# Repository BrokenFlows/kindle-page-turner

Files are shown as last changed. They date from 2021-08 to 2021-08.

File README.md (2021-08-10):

# Kindle Page Turner

Photo of Kindle Page Turner on a desk

The code in this repository, along with the physical components outlined in the [bill of materials](#Bill-of-Materials), can be used to turn pages of a Kindle e-reader with external buttons.

I made this project to allow me to more comfortably read books, something I struggle with as a result of chronic pain. I use my hands, in a relaxed position, to press the buttons. However, one could use longer wires and potentially press the buttons with their feet to avoid using arms at all.

Animatetd GIF of Kindle Page Turner on a desk

This project allows the user to turn pages on a Kindle using external buttons, when the kindle is in a stand.
Navigating the user interface of the Kindle is outside the capabilities of this project.

## Instructions
These instructions will serve as a rough guide of the steps required to make this project.
The project, as it stands, requires off-the-shelf electronic components, custom 3D printed pieces, and relatively simple soldering.

### Hardware
The [tools](#Tools) and [materials](#Bill-of-Materials) will be used to assemble the final product, shown above. If you have acquired the items required, you can follow the steps outlined in the [assembly](#Pre-Assembly) section.

#### Tools
- Soldering Iron
- Solder Wire
- 3D Printer/ 3D Printing Service/ or some means of mimicking [the case and parts](./stls/) listed below
- Scissors/ wire cutter
- **Optional:** wire stripper

#### Bill of Materials
Item # | Quantity | Part # | Part Name                                                                         | Description
------:|---------:|-------:|:----------------------------------------------------------------------------------|-------------
1      | 1        | G0910  | [Kindle](https://www.amazon.co.uk/dp/B07FQ4XCR1)                                  | The 10th Generation Kindle e-reader
2      | 1        | N/A    | [kindle_holder_and_servo_housing.stl](./stls/kindle_holder_and_servo_housing.stl) | A case for the Kindle
3      | 1        | N/A    | [pico_housing.stl](./stls/pico_housing.stl)                                       | The housing for the Raspberry Pi Pico at the back of the case
4      | 1        | N/A    | [pico_cover.stl](./stls/pico_cover.stl)                                           | A cover for the Raspberry Pi Pico Housing, to keep wires contained
5      | 1        | N/A    | [servo_horn_sheaths.stl](./stls/servo_horn_sheaths.stl)                           | For attaching stylus tips pads to the servo motors
6      | 2        | N/A    | [Stylus Pen Tips](https://www.ebay.ie/itm/174215638532)                           | Capacitive stylus tips for the touch screen
7      | 2        | SG90   | [SG90 Servo Motor](https://www.ebay.ie/itm/373323581713)                          | Servo motors for moving the stylus tips
8      | 1        | SCO915 | [Raspberry Pi Pico](https://www.raspberrypi.org/products/raspberry-pi-pico/)      | Raspberry Pi Pico Microcontroller
9      | 1        | N/A    | Micro-USB cable                                                                   | A power cable for the Raspberry Pi Pico
10     | 1        | N/A    | [Tablet holder](https://www.amazon.co.uk/gp/product/B074GNPSC7/)                  | **Optional:** Tablet holder for positioning the kindle at a comfortable height hands-free
11     | 6        | N/A    | [Wires](https://www.ebay.ie/itm/232901601951)                                     | Lengths of wire, to your preference (I used over 4 m of wire)
12     | 2        | N/A    | [Buttons](https://www.ebay.ie/itm/224192810260) or [Key Switches](https://splitkb.com/collections/switches-and-keycaps) | Buttons or Switches to push when wanting to turn the page on the Kindle — I use light-weight low-profile choc switches

#### 3D Printing
I recommend 3D printing the stl files at the following settings:
Setting         | Value
:---------------|-----:
Filament        | PLA
Nozzle Diameter | < 0.4 mm
Layer Height    | < 0.2 mm
Infill          | 20% <
Supports        | Off

#### Pre-Assembly
1. Place the servo motors into their respective housings, on the left and right sides of the Kindle housing, with their wires through the holes at the back. If the servos have connectors at the end of the wires, cut the connectors off before separating the wires by ~7 cm and stripping the ends.
2. Solder the button pins, that are connected when the button is pressed, to lengths of wire that are long enough to reach a desk or lap from where the Kindle will be used. I used 1m of wire to each button pin I was connecting.
3. To avoid the wires tangling, it is recommended that you twist, or secure at regular intervals, the wires used for the buttons.

We'll complete the assembly after dealing with the circuitry portion.

#### Circuit
In this section, we'll solder the circuit to match the following diagram:
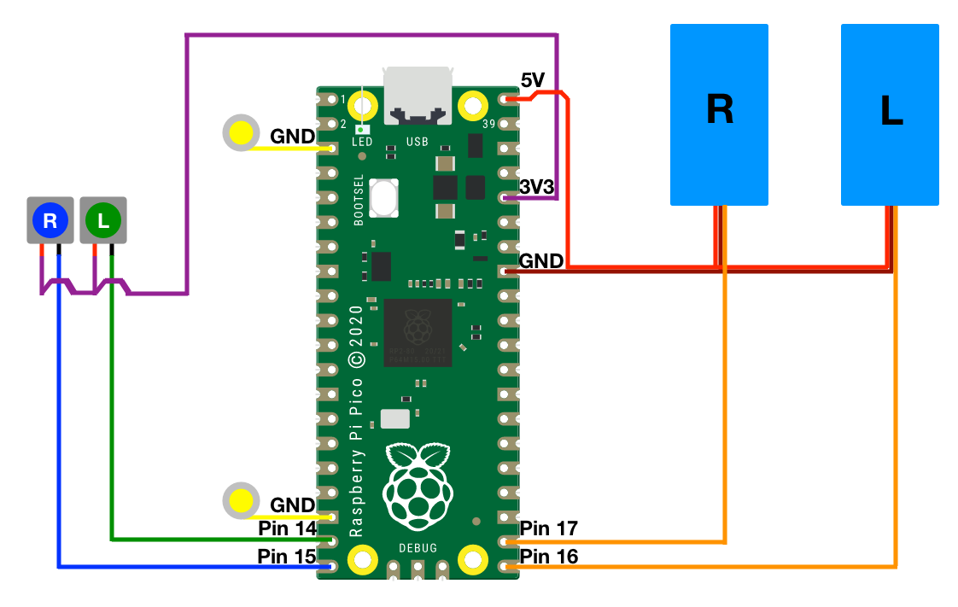
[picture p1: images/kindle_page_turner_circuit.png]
Circuit Diagram


- The buttons register a click when 3.3 V reaches their respective pins. The buttons are illustrated on the left side of the diagram.
- The stylus tips must be grounded for the Kindle to detect their taps. These are shown as the yellow lines and circles to the left of the Pico.
- The servos require 5 V to their red wires, their brown wires to be grounded, and their orange wires connected to the pins labelled on the right of the controller.

Use the [soldering tools](#Tools) to create mechanical and electrical connections between the components, as shown in the diagram.

#### Assembly
With the circuit ready, complete the following steps:
1. Feed the grounded wires through the servo horn sheaths. Make a connection here to the stylus tip, so that the tips will be grounded by the wires.
2. Secure the horns to the servos so that the end of their range will allow the stylus tip to reach the screen.
3. Put the servo horn sheaths, with wires and stylus tips attached, onto the servo horn.
4. Tidy the circuit into the Pico housing.
5. Slip the Pico Housing into the back of the Kindle case.
6. Cover the Pico and wiring with the housing cover.

At this point we will load the software onto the Pico.

### Software
I recommend following [this article](https://www.twilio.com/blog/programming-raspberry-pi-pico-microcontroller-micropython) on how to install micropython and transfer files onto the Raspberry Pi Pico.
If you copy [main.py](./main.py) onto the Raspberry Pi Pico, after installing micropython and setting up the hardware, it should allow buttons to turn the pages of the kindle.

### Testing
Once the software is loaded, each time the Pico is restarted it should flash a green LED for 1s. This will signal that the software was loaded successfully.
Then, you should try pressing the buttons to see if the servos move as expected.
If they do not, review the previous steps to resolve your issue.

It is recommended not to have your Kindle in the case when first testing, should the servos try to rotate past the screen.
If the rotation is off, reattach the servo horns to a better angle and try again.

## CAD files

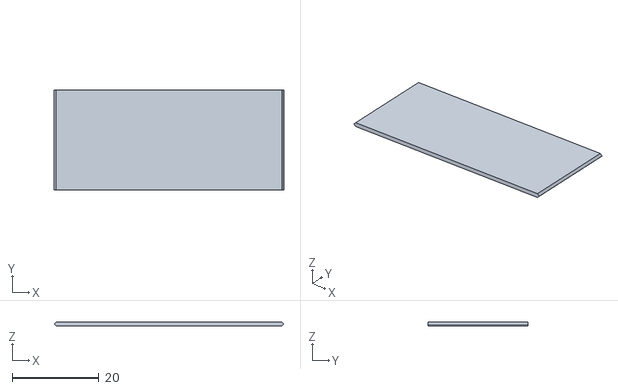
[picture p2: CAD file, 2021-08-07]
stls/pico_cover.stl
53.0 x 23.0 x 0.997

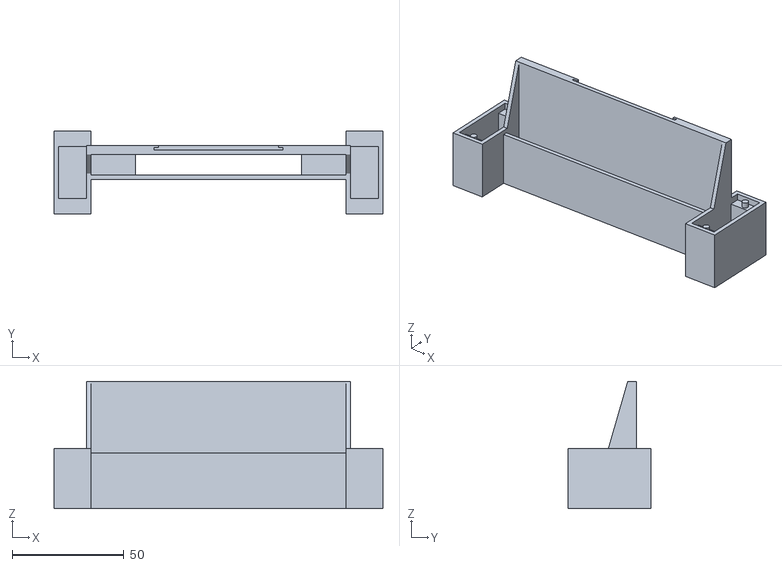
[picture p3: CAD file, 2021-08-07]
stls/kindle_holder_and_servo_housing.stl
147.5 x 37.0 x 57.0

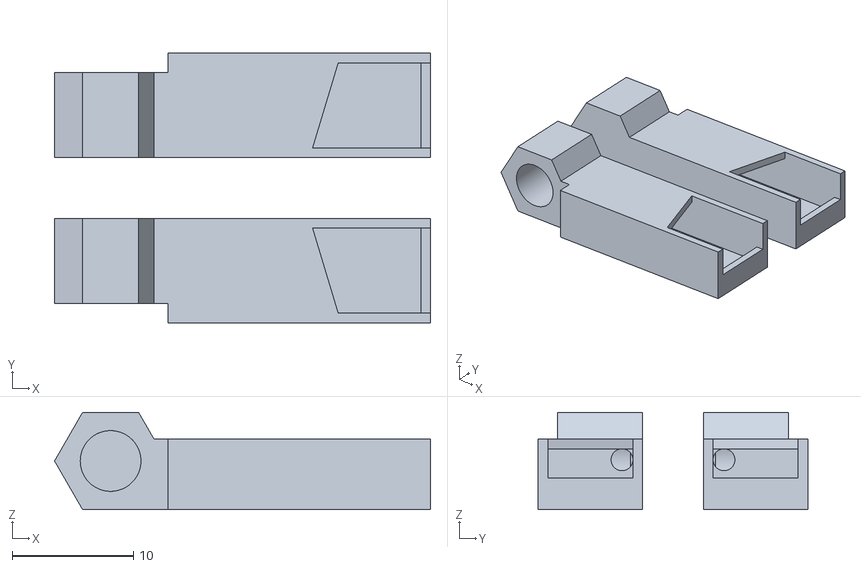
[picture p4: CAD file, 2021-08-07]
stls/servo_horn_sheaths.stl
31.0 x 22.2 x 8.00

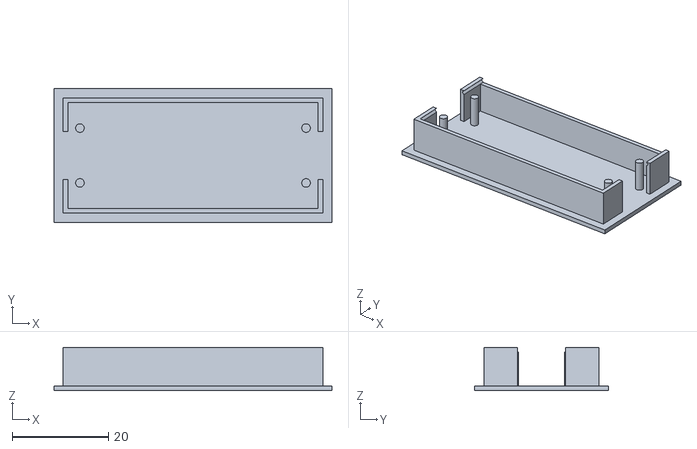
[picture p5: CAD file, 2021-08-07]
stls/pico_housing.stl
57.8 x 27.8 x 9.00

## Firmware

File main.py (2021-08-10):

from machine import Pin
from machine import PWM
from utime import sleep, sleep_ms

# set pins for button and led
right_button = Pin(15,Pin.IN,Pin.PULL_DOWN)
right_servo_pin = 17
left_button = Pin(14,Pin.IN,Pin.PULL_DOWN)
left_servo_pin = 16
led = Pin(25, Pin.OUT)
frequency = 50

# servo durations for target positions
home_right = 1300000
screen_right = 500000
home_left = 1600000
screen_left = 2500000

# servo wait durations in ms
wait_dur = 250

# blink led to show power on
led.on()
sleep(1)
led.off()

def screen_tap(servo_pin, frequency, screen_pos, home_pos, wait_ms):
    servo = PWM(Pin(servo_pin)) # set servo pin

    # define the frequencies used for the servo motors
    servo.freq(frequency)

    servo.duty_ns(screen_pos) # move servo to screen 
    sleep_ms(wait_ms) # wait for tap to register
    servo.duty_ns(home_pos) # re-home servo
    sleep_ms(wait_ms) # wait for re-home

# constantly wait for input, and tap screen accordingly
while True:
    if right_button.value():
        screen_tap(right_servo_pin, frequency, screen_right, home_right, wait_dur)
    elif left_button.value():
        screen_tap(left_servo_pin, frequency, screen_left, home_left, wait_dur)

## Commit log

2021-04-09 adds a version of main.py that tests IO before servos arrive and testing can begin with them
2021-08-06 adds servo motion on button press
2021-08-07 adds delay for servo to re-home
2021-08-07 moves servo motion to functions
2021-08-07 adds the stl files for the 3DP case
    [kindle_holder_and_servo_housing.stl, pico_cover.stl, pico_housing.stl, servo_horn_sheaths.stl]
2021-08-07 adds images directory and circuit diagram
2021-08-07 adds further instructions to the README — may need images
2021-08-07 fixes some text layout and flow
